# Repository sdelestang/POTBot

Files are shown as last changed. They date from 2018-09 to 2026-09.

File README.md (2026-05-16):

# POTBot

**Smart camera systems for tracking climate change underwater in fish and habitats.**

POTBot is an open-source, Arduino-based automated underwater camera and environmental monitoring system. Originally developed for deployment inside commercial western rock lobster pots, the system records video of marine habitats and faunal communities at fishing locations, logs water temperature, and captures GPS coordinates on retrieval.

The system operates autonomously for approximately one month of continuous fishing activity. When spent, units are simply swapped out for fresh ones and data collection continues at minimal cost.

## How It Works

1. **Power on** — the unit acquires a GPS lock and enters standby.
2. **Deployment** — a conductivity-based wet switch detects immersion and triggers video recording.
3. **In water** — the camera records for a configurable duration (default 40 min). Water temperature is logged periodically. If deployed in darkness, a short supplementary video is recorded at dawn.
4. **Retrieval** — when removed from water, the GPS activates and records the pot's position.
5. **Data download** — videos are accessed via USB from the Mobius camera; metadata (GPS, timestamps, temperatures) is read through the Arduino Serial Monitor.

## Repository Structure

```
POTBot/
├── docs/
│   ├── POTBot_Operations_Manual.docx   # Full setup and operations manual
│   └── Flow_Diagram_PB_IV.jpg          # Operational state diagram
├── Version10/
│   └── PB_CodeV10/
│       └── PB_CodeV10.ino              # Current firmware (V10)
├── Pot_code/                           # Earlier firmware versions
├── Final-Report 2011-021.pdf           # Original FRDC research report
└── README.md
```

## Hardware

| Component | Description |
|-----------|-------------|
| Microcontroller | Adafruit ItsyBitsy M0 Express |
| Camera | Mobius ActionCam |
| GPS | Serial GPS module (9600 baud) |
| Real-Time Clock | Gravity RTC (I²C) |
| Temperature Sensor | Dallas DS18B20 (OneWire) |
| Flash Storage | Adafruit SPI Flash (onboard FAT filesystem) |
| Status LED | Adafruit DotStar |
| Wet Switch | Conductivity-based (analog) |

## Getting Started
### Download all files inclusing the manual
Download the firmware from GitHub. Navigate to https://github.com/sdelestang/POTBot and click the green “Code” button, then select “Download ZIP”. Save and extract the ZIP file to a convenient location on your computer (e.g. C:\POTBot).

### Prerequisites

- [Arduino IDE](https://www.arduino.cc/en/software) (latest version)
- Adafruit SAMD board support (install via Boards Manager)
- Required libraries (install via Library Manager):
  - OneWire
  - DallasTemperature
  - Adafruit SleepyDog
  - Adafruit SPIFlash
  - TinyGPS++
  - Adafruit DotStar
  - RTClib
- GravityRTC library (install from ZIP — included in the repo or available in the docs)

### Upload Firmware

1. Open `Version10/PB_CodeV10/PB_CodeV10.ino` in Arduino IDE.
2. Select **Adafruit ItsyBitsy M0** as the board.
3. Select the correct COM port.
4. Click Upload.

For detailed setup, deployment, and data retrieval instructions, see the **[Operations Manual](docs/POTBot_Operations_Manual.docx)**.

## Configurable Parameters

| Parameter | Default | Unit | Description |
|-----------|---------|------|-------------|
| `VidTime` | 2400 | seconds | Video recording duration after deployment |
| `GPSTime` | 240 | minutes | GPS active time after retrieval |
| `Dawn` | 7 | hour (24h) | Start of daylight window |
| `Dusk` | 17 | hour (24h) | End of daylight window |

## Applications

POTBot systems have been used to:

- Augment spatial habitat mapping off the west coast of Western Australia
- Document spatial and habitat distributions of marine teleosts across the west coast bioregion
- Serve as a robust, automated alternative for BRUV (Baited Remote Underwater Video) monitoring with geographic synchronisation of footage

## Licence

This project is open-source freeware. See individual files for any specific terms.

## Contributing

Contributions, bug reports, and feature requests are welcome. Please open an issue or submit a pull request.

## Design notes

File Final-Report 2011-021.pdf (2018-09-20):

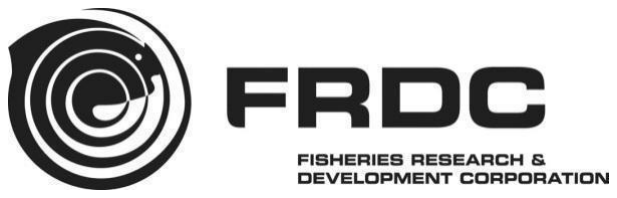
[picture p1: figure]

1

# Development of an industry-based habitat mapping/monitoring system

Matthew Pember, Simon de Lestang and Dirk Slawinski

2017

FRDC Project No 2011/021

2

© Year Fisheries Research and Development Corporation. All rights reserved.

ISBN [Insert ISBN/ISSN – researcher to obtain - TBA]

Development of an industry-based habitat mapping/monitoring system 2011/021

2017

Ownership of Intellectual property rights
Unless otherwise noted, copyright (and any other intellectual property rights, if any) in this publication is owned by the Fisheries Research and Development Corporation.

This publication (and any information sourced from it) should be attributed to Pember, M., de Lestang, S. & Slawinski,
D. Department of Primary Industries and Regional Development; Fisheries Division, Western Australia, 2017, Development of an industry-based habitat mapping/monitoring system, Perth, Western Australia, July.

Creative Commons licence
All material in this publication is licensed under a Creative Commons Attribution 3.0 Australia Licence, save for content supplied by third parties, logos and the Commonwealth Coat of Arms.

Creative Commons Attribution 3.0 Australia Licence is a standard form licence agreement that allows you to copy, distribute, transmit and adapt this publication provided you attribute the work. A summary of the licence terms is available from creativecommons.org/licenses/by/3.0/au/deed.en. The full licence terms are available from creativecommons.org/licenses/by/3.0/au/legalcode.

Inquiries regarding the licence and any use of this document should be sent to: frdc@frdc.com.au

Disclaimer
The authors do not warrant that the information in this document is free from errors or omissions. The authors do not accept any form of liability, be it contractual, tortious, or otherwise, for the contents of this document or for any consequences arising from its use or any reliance placed upon it. The information, opinions and advice contained in this document may not relate, or be relevant, to a readers particular circumstances. Opinions expressed by the authors are the individual opinions expressed by those persons and are not necessarily those of the publisher, research provider or the FRDC.

The Fisheries Research and Development Corporation plans, invests in and manages fisheries research and development throughout Australia. It is a statutory authority within the portfolio of the federal Minister for Agriculture, Fisheries and Forestry, jointly funded by the Australian Government and the fishing industry.

Researcher Contact Details | FRDC Contact Details
Name: Matthew Pember Senior Resource Access Officer Address: 56 Marine Tce, Fremantle 6160 WA Phone: +61 08 9432 7777 Fax: +61 08 9432 7700 Email: rao@wafic.org.au | Address: Phone: Fax: Email: Web: 25 Geils Court, Deakin 2600 ACT 02 6285 0400 02 6285 0499 frdc@frdc.com.au www.frdc.com.au ,

In submitting this report, the researcher has agreed to FRDC publishing this material in its edited form.

3

## Contents

Acknowledgments | 6
Abbreviations | 6
Executive Summary | 7
Introduction | 11
Objectives | 12
Methods/Results | 13

Objective 1. Development of a cost-effective system for obtaining geo-referenced environmental
information. | 13
POTBot functionality | 14
POTBot development | 14
Initial design | 14
Component Choice | 16
Controller | 16
Camera | 16
GPS | 20
Temperature Sensor | 21
Data Storage | 21
Power Source | 21
Additional Supporting Components | 22
Water Proof Housing | 22
Placement in a lobster pot | 24
Physical layout and construction | 24
Programming | 26
Objective 2. Trial implementation of system by industry to test concept. | 27
Performance of POTBot v2 and 3 | 29
Objective 3. Cost-benefit analysis with conventional ground-truthing techniques. | 30
Comparison of habitat mapping at the Leeman Closed area | 30
Comparison of visual-based fin-fish monitoring | 33
Discussion | 35

Objective 1: Development of a cost-effective system for obtaining geo-referenced environmental

4

information. | 35
Objective 2: Trial implementation of system by industry to test concept. | 36
Objective 3: Cost-benefit analysis with conventional ground-truthing techniques. | 37
Conclusion | 38
References | 39
Implications | 41
Recommendations | 41
Further development | 41
Extension and Adoption | 41
Project Coverage | 42
Project Materials Developed | 43
Appendix 1. | 44
Appendix 2. POTBot code. | 45

## Tables

Table 1. List of the potential functionality of the POTBot and their associated importance, cost and difficulty of implementation. Grey rows represent functions chosen for implementation into the initial
model. | 20
Table 2. Spy camera trialled and their respective picture qualities. The camera chosen for integration
into POTBot v1 Is highlighted in grey. | 23
Table 3. Upgraded cameras for use in POTBot versions 2-4. | 25
Table 4. Component costs for the development of POTBot version 3. | 30

## Figures

Figure 1. Evolution of the various versions of the POTBot. | 19
Figure 2. Wiring schematic of the POTBot, with permanent connections shown as solid lines and intermittent connections as dotted lines. Red, black and blue lines denote positive, negative and serial (data) connections, respectively. Transistors (T) and resistors (R) are shown. The external wires shown at the middle right are the wires running to the external of the water housing to detect the presence of water.
| 24
Figure 3. Schematic of the PCB board for the POTBot. | 29
Figure 4. Flow diagram showing business rules followed by the POTBot versions 1-3 and its subsequent

5

behaviour. | 32
Figure 5. Map illustrating the spatial distribution of more than 1300 pot camera deployments made during research and normal commercial lobster fishing activities. The inset shows the key habitat categories observed inside and surrounding the research area at Leeman that is closed to lobster fishing and where
high resolution bathymetric information was collected as part of FRDC 2008/013. | 34
Figure 6. Relative causes resulting in a habitat classification not occurring from a POTBot deployment. | 35

## Plates

Plate 1. Breadboard linking power to an integrated circuit and an 808 camera, using a signal relay to connect a junction across the shutter button on the camera (paired white wires) (photo from
http://quinndunki.com/blondihacks/?p=925). | 17
Plate 2. High-pressure PVC pipe fitting housings used in POTBot v 2 and 3, showing clockwise from top right; entire housing with black screw cap on left, water sensing screw pins towards the centre and lens located on the right; closer shot of the water sensing screw pins with associate glue to ensure a tight seal; internal view of the housing showing the wires connected to the internal aspect of the screw pins; front of
the housing with its clear Perspex lens. | 23
Plate 3. Schematic of a lobster pot showing the location of the POTBot. | 29
Plate 4. POTBot built on purpose-made PCB (green) with camera at the front, GPS visible towards the back and battery and Arduino mini located under the PCB; PVC underwater housing capable of deployments to
greater than 180 m. | 30

6

## Acknowledgments

We would like to thank Fisheries Research and Development Corporation for their financial support and all

of the commercial rock lobster fishers who agreed to run POTBot systems in their fishing gear. We would

also like to thank Ainslie Denham for help with the geo-statistical work in this report and Lachlan Strain,

Scott Evans, Nick Blay and Nick Caputi for their help in reviewing.

## Abbreviations

BRUVs: Baited Remote Underwater Video Systems

CSIRO: The Commonwealth Scientific and Industrial Research Organisation.

DPIRD FD: Department of Primary Industries and Regional Development, Fisheries Division. Western Australia

FRDC: Fisheries Research and Development Corporation

MSC: Marine Stewardship Council

NMEA: National Marine Electronics Association

PCB: Printed Circuit Board

PCM: Pulse Code Modulation

POTBot: Pictures Of The Bottom

UWA: University of Western Australia

WCRLMF: West Coast Rock Lobster Managed Fishery

WAMSI: West Australian Marine Science Institution

7

## Executive Summary

Mapping / monitoring in the marine environment can be a very costly exercise. Scientists from the

Department of Primary Industries and Regional Development; Fisheries Division (FD) and the

Commonwealth Scientific and Industrial Research Organisation (CSIRO) have developed a small, low-cost

automated camera system that, when fitted to commercial fishing gear, can achieve this at minimal cost.

The POTBot (Pictures Of The Bottom) system is a cheap, small “smart” camera that can track its position

globally and the date and time, and can record high-definition video and water temperature readings when it

determines it has been deployed into the ocean.

Initially developed to be attached to pots in the West Coast Rock Lobster Managed Fishery (WCRLMF), the

POTBot system collects vision of the habitats and the faunal communities where fishing gear has been set,

and lasts for about a month of continuous commercial lobster fishing activity. When out of power, systems

are simply swapped out for fresh ones / recharged and the collection of data continues at minimal costs.

Trials of the POTBot system conducted during this study have proved extremely valuable and have been

used to augment the development of a number of spatial habitat maps off the west coast of Western

Australia, as well as document the spatial and habitat distributions of a number of marine teleosts

throughout the west coast bioregion. The POTBot systems have also proved to be a very valuable system

for use in Baited Remote Underwater Video Systems (BRUVs) monitoring due to their robustness,

automated capabilities and the geographic synchronisation of their footage.

The success of this project is highlighted by current plans to incorporate POTBot systems on a long-term

basis into standard research programs: Western Rock Lobster monitoring program, FD BRUV monitoring

programs and two recently approved Fishery Research and Development Corporation (FRDC) projects

being conducted by the University of Western Australia (UWA). A number of interstate and overseas

research institutes have also shown interest in obtaining this technology for use in their own research

environments.

Background

A thorough appreciation of the nature and extent of the habitats a fishery operates across, and possibly

impacts upon, is fundamental to the effective implementation of ecosystem-based fisheries management.

The significance of reliable habitat information to sustainable management is highlighted by the fact that it

may be considered a prerequisite for fisheries seeking to obtain, or retain, ecologically sustainable

certification such as Marine Stewardship Certification (MSC).

In the case of the Western Rock Lobster Panulirus cygnus, current and recently completed projects (FRDC

2004/049, 2008/013) and the West Australian Marine Science Institution (WAMSI) node 4.3 (Corals of the

northwest of Western Australia) have illustrated that the composition of benthic habitats may have a strong

influence on the demographics of exploited species. While these projects provided high resolution

8

information on benthic habitats at key locations, areas currently mapped at high resolution represent < 1% of

the WCRLMF. The ability to expand mapping at a similar resolution was constrained by the large costs

involved with current mapping techniques, e.g. multibeam sonar. In a recent audit report the MSC certifying

body accepted the futility of expanding these surveys with high cost techniques and suggested a more

broad-scale approach should be adopted in mapping the distribution of habitats in the WCRLMF.

Aims / Objectives

This project aimed to develop and trial the implementation of a cost effective tool for the ongoing collection

of geo-referenced environmental information, including data on the composition and distribution of benthic

habitats. The concept arose from the realisation that opportunities exist for greater industry involvement in

collection of oceanographic and habitat data. Commercial Wester Rock Lobster fishers set pots on a daily

basis and low-cost technologies are now available that have the potential to give them the ability to collect

high resolution habitat data. Information could be collected across a broad spatial scale with no added cost

or interruption to their fishing operation. The key objectives of the study were:

1. Development of a cost-effective system for obtaining geo-referenced environmental information.
2. Trial implementation of system by industry to test concept.
3. Cost-benefit analysis with conventional ground-truthing techniques.

Methodology

The project focussed on each objective sequentially. As such initial work was conducted on developing a

POTBot system prototype. The requirements for the system were determined through interviews with

marine scientists. The POTBot was designed to undertake a range of programmed tasks based on its

detection of the presence of seawater (e.g. if the system was submerged or not).

Testing of prototypes was conducted in two phases: Initial laboratory testing and extended in situ testing.

a) Initial testing / selection of components was conducted within the laboratory (aquaria) at FD. This included

activities such as submersion tests, image quality, power consumption and accuracy of measurements (e.g.

global position and water temperature).

b) Extended testing was conducted in the field on board FD research vessels. This examined the

components under working conditions and allowed for the refinement of programming to the behaviour of

typical fishing operations.

Trial implementation of the system by industry followed on after FD field trials. A number of interested

commercial Wester Rock Lobster fishers spanning the WCRLMF were provided with POTBot systems (~20

fishers) between 2012 and 2015. These trials tested the robustness of the POTBots to a commercial fishing

operation, commercial fisher’s acceptance of units in their pots and collected initial habitat information

9

throughout the WCRLMF.

A cost-benefit analysis comparing the POTBot system with conventional ground-truthing techniques was

then conducted to help assess the value of implementing an on-going monitoring program using the system.

As part of FRDC project 2008/013, a deep-water location in the WCRLMF was ground-truthed using the

traditional techniques of drop-camera and towed video. These data and their associated costs have been

fully recorded by the FD. As additional monitoring of the lobster population in this area occurs annually, it

proved an ideal opportunity to fit POTBot systems into these pots and re-map the area using this innovative

technology at no extra cost. The two sets of ground-truthed data were compared via geostatistical

techniques, with indicator variables of the presence or absence of each habitat type being compared. The

cost associated with the collection of the two sets of data was also compared.

A second cost-benefit analysis was undertaken following the use of POTBot videos to conduct an

assessment of the spatial and temporal distributions of a number of key teleosts along the western

Australian coast, from Kalbarri in the north to Mandurah in the south (Brooker et al. submitted). This study

was compared to a study with a similar spatial coverage based on BRUV systems (Langlois et al., 2012).

Again the ability of the two studies to determine teleost distributions and their associated costs have been

compared.

Results / Key findings

This project was successful in developing a low cost automated geo-referencing camera system that can be

deployed throughout a number of commercial fishing operations (i.e. operations which deploy fishing gear).

At a unit cost of approximately $250 this technology is far more accessible for wide-scale implementation

than other, less autonomous products available (e.g. GoPro at ~$500 unit⁻¹
).

The success of developing the POTBot was partly attributable to the recent rapid increase in the

development of micro-electronic systems and robotics. Over the course of the project both lithium-polymer

batteries and high-definition “spy” cameras became widely available in a range of sizes and at markedly

reduced prices. Micro-controllers have also increased in their diversity and reduced in cost. This has

allowed the POTBot to maintain a small size as well as low cost.

Analysis of both research and industry collected data is continuing. The collated habitat information has

provided a map of the key habitats fishers operate across the extent of the WCRLMF and is currently being

used to validate the fishery-wide habitat maps that have been developed from the outputs of a previous

FRDC project (2008/013). These projects have directly resulted in the MSC re-certification of the Western

Rock Lobster Fishery becoming free, for the first time, of any conditions under Principle 2 (Minimising

environmental impact: What are the impacts? Fishing activity must be managed carefully so that other

species and habitats within the ecosystem remain healthy). These projects have shown that there are no

discernible impacts on the wider ecosystem from the Western Rock Lobster fishery.

10

Examination of fish community data from POTBot deployments highlighted the units’ versatility and cost-

effectiveness as a fisheries monitoring tool that can be deployed using existing infrastructure. Although

comparison against spatio-temporal variation in similar fisheries-independent or -dependent indices is

required, preliminary results suggest that the method has potential as an alternative means for monitoring

relative abundance of fin-fish.

POTBots were capable of producing data used to develop a habitat map that showed good agreement to a

fine-scale high resolution map produced by combining a number of different methods including expensive

side-scan sonar. This comparison shows that the use of POTBots can produce habitat maps far cheaper

than can be produced based on the more traditional techniques of towed video and drop camera, especially

if an area is to be fished for a separate purpose (e.g. fishery survey). Furthermore, the comparison with a

BRUV fin-fish project suggests that the monitoring of marine fauna can also be conducted using POTBots at

a fraction of the cost, so long as the area of the study is shared with a commercial fishery willing to adopt the

POTBot fishing program.

Recommendations

The POTBot system developed during this study proved to be an extremely useful research tool. This has

been highlighted by the fact that data collected during this project has already been used to describe the

faunal composition of teleosts along the mid-west coast of Australia, as well as to augment the development

of habitat maps throughout the same area. Through the use of this technology, information on habitats in

remote areas has been recorded for the first time, information that will be valuable when determining long-

term environmental changes in the future. Such a case has already occurred following the marine heatwave

of 2010/11. It is recommended that, when appropriate, this technology be adopted by other research

institutions to gather this previously inhibitively expensive data and long term data sets should start to be

collated.

Keywords

Camera, POTBot, BRUV, marine, habitat, mapping, lobster fishery

11

## Introduction

A thorough appreciation of the nature and extent of the habitats a fishery operates across, and possibly

impacts upon, is fundamental to the effective implementation of ecosystem based fisheries management.

Understanding the relationships between benthic habitats and the species they support not only allows

fishery managers to control against any potentially undesirable impacts on habitats, but also permits

management to be more adaptive and spatially explicit. The significance of reliable habitat information to

sustainable management is highlighted by the fact that it may be considered a prerequisite for fisheries

seeking to obtain, or retain, ecologically sustainable certification, i.e. MSC certification.

In the case of the Western Rock Lobster Panulirus cygnus, current and recently completed projects

(FRDC 2008/013, 2004/049 and WAMSI 4.3) have illustrated that the composition of benthic habitats may

have a strong influence on the demographics of exploited species. While these projects provided high

resolution information on benthic habitats at key locations, areas currently mapped at high resolution

represent < 1% of the WCRLMF. The ability to expand mapping at a similar resolution is constrained by the

large costs involved with current mapping techniques, e.g. multibeam sonar. In a recent audit report the MSC

certifying body accepted the futility of expanding these surveys with high cost techniques and suggested a

more broad-scale approach should be adopted in mapping the distribution of habitats in the WCRLMF.

This project aims to develop and trial the implementation of a cost effective tool for the ongoing collection of

geo-referenced environmental information, including data on the composition and distribution of benthic

habitats. The concept arose from the realisation that opportunities exist for greater industry involvement in

collection of oceanographic and habitat data. Commercial Western Rock Lobster fishers are setting pots in

benthic habitats on a daily basis and low-cost technologies are now available that have the potential to give

them the ability to collect high resolution habitat data. Information could be collected across a broad spatial

scale with no added cost or interruption to their fishing operation.

The cost effectiveness of this system is the product of an innovative use of relatively inexpensive technology

and the direct involvement of stakeholders in data collection. Recently, fishers have participated in a study

using modified research pots where the location of pot sets is recorded along with catch information. In

addition to detailed demographic data, that project is beginning to provide researchers with a broad-scale

picture of the spatial distribution of fishing operations across different parts of the WCRLMF and fishing

season. Outputs of the modified pot trials could be greatly expanded if habitat information could be easily

collected for each pot set.

Besides informing researchers and managers of the broad-scale habitat patterns found across the

WCRLMF, this system could represent a cost-effective method of collecting the habitat information required

to validate predictive habitat models. Furthermore, the information provided will fine-tune habitat / Western

Rock Lobster relationships developed in previous projects. Wide and continuous deployment of systems

throughout the WCRLMF will allow researchers to quantify how such relationships change with latitude and

12

depth and vary temporally.

In addition to mapping habitat, these technologies are capable of collecting a range of other important data

including spatial information on salinity, water temperature and depth, and the relative abundance / species

composition of finfish. Ultimately, increased knowledge of the interactions between the environment and

exploited species will foster more holistic and adaptive fisheries management. While the project concentrates

on the fishery for the Western Rock Lobster in a proof of concept study, the technologies have far wider

applications, particularly for small or data poor fisheries.

A thorough understanding of the relationships between benthic habitats, exploited species and the fisheries

they support increases the capacity for fisheries management to be ecologically sustainable and adaptive in

the face of climate change and spatial zoning.

Improving knowledge of such relationships typically requires a significant commitment of resources, i.e.

swath-mapping and dedicated ground truthing. Costs are prohibitive of continuous spatial coverage and the

snap-shot nature of data acquisition provides little confidence that habitat relationships persist through time.

There is a real need for a more cost-effective approach to collecting oceanographic and habitat information.

This project develops and implements a system capable of providing constantly updating, geo-referenced

environmental data, including information on the composition of benthic habitats.

This project addresses key priorities of FRDC’s Ecological Sustainable Development theme. Specifically, the

project will:

- develop a cost-effective tool that aids in the implementation of ecosystem-based fisheries management.
- improve the acquisition and incorporation of environmental / habitat data into fisheries management.
- improve knowledge of key biological attributes for target species.

In addition, this project contributes to other environment related RD&E priorities by:

- informing on the likelihood, and thus mitigating the impacts, of fishing activities on aquatic habitats and

ecosystems.

- providing a tool to monitor fishing gear interactions with non-target species.
- contributing to industry’s ability to adapt to climate change by providing a tool to monitor real-time changes

to oceanographic conditions, benthic habitats and relationships with exploited species.

In the case of the Western Rock Lobster, this research ensures continued MSC certification by addressing

requirements that “the nature and distribution of habitats relevant to the fishing operations is known”.

However, the needs addressed by the project are not specific to the WCRLMF. This technology is

transferable to other fisheries and has particular application to data poor fisheries.

## Objectives

1. Development of a cost-effective system for obtaining geo-referenced environmental information.
2. Trial implementation of system by industry to test concept.
3. Cost-benefit analysis with conventional ground-truthing techniques.

13

## Methods/Results

## Objective 1. Development of a cost-effective system for obtaining geo-referenced

environmental information.

The cost-effective system for obtaining geo-referenced environmental information has been named POTBot.

The model that was used for field trials and the cost-benefit analysis was the third product in a series of

prototypes that were developed. The evolution of the various prototypes was due to the concurrent

expansion and increase in accessibility of micro-computers, batteries and camera systems. What was

available and possible at low cost towards the end of the project was substantially different from what was

available at the beginning. The evolution in development of the POTBot is shown in Figure 1 and described

below.

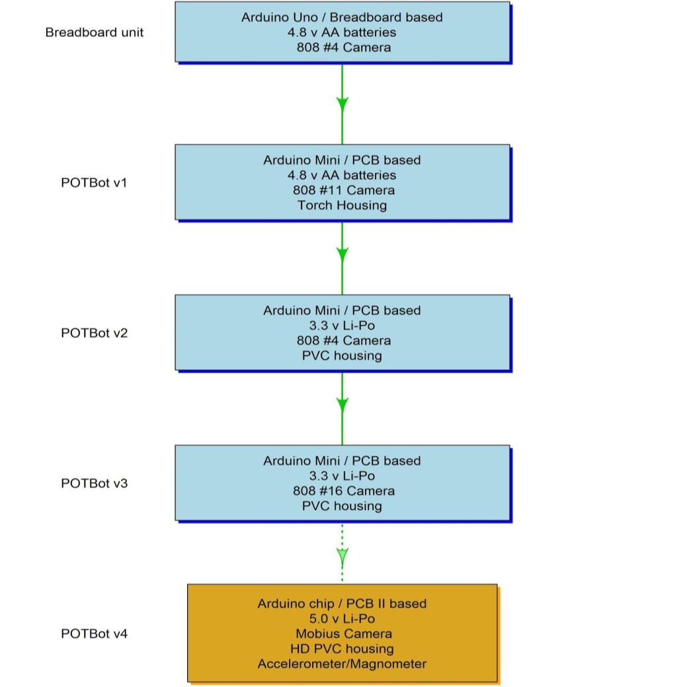
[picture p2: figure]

Figure 1. Evolution of the various versions of the POTBot. Note version 4 was developed subsequent to the analyses described in this report.

14

POTBot functionality
In order to develop the camera system, literature and internet reviews were first conducted to determine what

functions were available that could be incorporated into the system. This included contacting other marine

researchers to see what was on their “wish list” for such a device. The potential functionality of a POTBot

system was then compiled from the reviews along with their associated general costs and ease of

implementation (Table 1).

Table 1. List of the potential functionality of the POTBot and their associated importance, cost and difficulty of implementation. Grey rows represent functions chosen for implementation into the initial model.

Functionality | Importance | Implementation Difficulty | Relative cost
Good quality vision (1280 x 720 pixels) | 3 | 1 | 2
High Definition vision (1920 x 1080 pixels) | 2 | 2 | 2
Stereo vision (twin lenses) | 1 | 2 | 2
Determine position (GPS) | 3 | 1 | 2
Lights | 1 | 3 | 2
Data storage | 3 | 1 | 1
Measure temperature | 2 | 1 | 1
Measure salinity | 1 | 3 | 2
Measure depth | 2 | 3 | 3
Measure orientation / movement | 1 | 1 | 1
Measure water movement / current | 1 | 3 | 3
Depth rated to 100 m | 3 | 1 | 1
Depth rated to 200 m | 2 | 2 | 2
Depth rated to 1000 m | 1 | 3 | 3
Small size | 3 | 2 | 2
Long battery life (>30 days) | 3 | 3 | 2
Ease of use | 3 | 2 | 2
Blue-tooth connectivity | 1 | 3 | 3
Wireless charging | 1 | 3 | 2

1 = low, 2 = medium, 3 = high

From the review process it was considered possible that a basic model could be developed that contained all

of the high priority functions fairly easily (grey rows in Table 1). As such it was decided to initially develop

this basic version for trials prior to examining the possibility of upgrading various aspects. The initial model

included the capabilities of the functions highlighted by the grey rows in Table 1 (POTBot v1).

POTBot development

Initial design
Once the general capabilities of the system had been determined a second review process was undertaken

15

to determine whether:

- a system such as POTBot v1 currently existed;
- a similar system existed that could be modified to suit our purposes;
- the components of POTBot v1 existed and could be amalgamated to suit our purposes;
- the components did not all exist and some would have to be built from the ground-up.

A number of camera systems were available for sale, of which some were water proof (with associated

housings), some were programmable and could geo-reference images/video, some were small and some

had low power demands. However, no pre-made systems were found that provided the entire functionality of

POTBot v1.

A number of systems that had similar functionality to POTBot v1 already existed and essentially only needed

waterproof housings developed. These systems were smart phones. They contain cameras with geo-

referencing capabilities, magnetometers and accelerometers to determine orientation and acceleration,

respectively, and data storage capabilities. They also could utilise external power sources to extend their

run-time into weeks. There were however, two main limitations to adapting a smart phone into POTBot v1.

They are relatively expensive (> $400 per unit) and they required custom-made waterproof housings. A

housing to fit a rectangular object with a camera on its largest face (standard smart phone layout) requires

either a rectangular housing or a relatively large cylindrical housing. An objective of the project was to

develop a small unit so the large cylindrical housings were not considered appropriate. Rectangular

housings presented structural issues for deployment at depth and were therefore very difficult and expensive

to construct (> $300 per unit). The programming of mobile phones further requires specialised skills as their

software platforms have very technical solutions to problems such as power saving, which are quite difficult

to modify to suit the requirements of the POTBot v1. As such it was not considered the best course of action

to re-purpose a smart phone.

The various components of the POTBot v1 system were found to already exist, with the majority of functions

capable of being completed by a number of different components, thus providing choice. This diverse range

of products available allowed their accessibility and cost to be factored into whether they were chosen to be

integrated. For example, for the video camera alone over 50 products fitted the brief of being small,

providing a minimum of 1280 x 720 pixel resolution, having relatively low power demands, being externally

controllable and having a relatively low cost. Another advantage of integrating specific components was the

removal of superfluous components with their associated power demands. For example, a smart phone will

poll for and analyses phone signal coverage strength. This unnecessarily utilises power and is not required

for integration in the POTBot v1. Therefore the option of combining specific components proved to be the

most power conservative. The development of POTBot v1 from pre-existing components was chosen as the

best model.

16

Component Choice

Controller
To achieve the chosen functionality of POTBot v1 the system needed a camera, GPS, temperature sensor

(thermistor), data storage unit, power source and water proof housing. The system also needed a central-

controlling unit, something to turn the camera on and off, determine the geographic position and record this

information. Of the available options it was initially clear that one of the many micro-controllers available was

a good option ($15 - $50), with the open-source nature of their software and large communities providing

online scripting help. Controllers compared were the BeagleBone units (https://beagleboard.org/), Raspberry

Pi units (https://www.raspberrypi.org/) and Arduino units (https://www.arduino.cc/). Generally the three

platforms had similar functionalities and capabilities, with the main difference being the Arduino’s lower

power usage (due in part to its lower processor power). The Arduino also had the ability to enter into a sleep

mode, thus further reducing (66%) its power usage. The very small footprint of the Arduino Mini, its low cost

(~$15) and its ability to run on either 3.3 or 5 v made this board our choice for controlling the POTBot v1

(https://www.arduino.cc/en/Main/arduinoBoardMini). However, due to the mini’s small size and design, an

Arduino Uno (https://www.arduino.cc/en/Main/ArduinoBoardUno) was initially used for the development and

solderless bread boarding of POTBot v1 (Plate 1; a board containing a number (+50) of interconnected pins

that allow easy connection of a number of wires/components: see https://en.wikipedia.org/wiki/Breadboard

for more information on breadboards). The main features of the Uno that made it more appropriate for the

development stage was its pin structure, which did not require soldering (header pins are pre-built) and the

easier serial connection of the Uno to the computer for two-way communication (i.e. uploading software and

receiving Arduino outputs).

Camera
A number of small camera units were examined and trialled. The recent boom in the prevalence of small

low-cost spy-cameras proved beneficial for this project. The benefits of these camera units was that they

were all very cheap ($1 - $40) and small (< 50 mm long and <10 mm thick), they contained very advanced

post processing software for compressing large video files and storing all of the footage on small microSD

cards, they all use 3.3 v power sources (can generally handle from 3 – 5 v) and their usage is simplified

(minimal button presses to take and stop video footage). The only real limitation of these cameras was the

quality of some of the unit’s footage (even though they were described as 1280 x 720 px). As such twelve

commonly advertised “spy” cameras were purchased and trialled. A list of these initial cameras trialled, their

cost and sources are listed in Table 2.

Of the twelve spy cameras trialled the Mini 808 Car Key Chain Micro Camera HD 720P #4 was chosen for

integration into POTBot v1 due to its good quality video and low price ($25). This camera contained two

push-button switches to turn it on and off and to start and stop videos being recorded. This camera could be

controlled by the micro-controller board through the soldering of two wires onto opposite poles of each of the

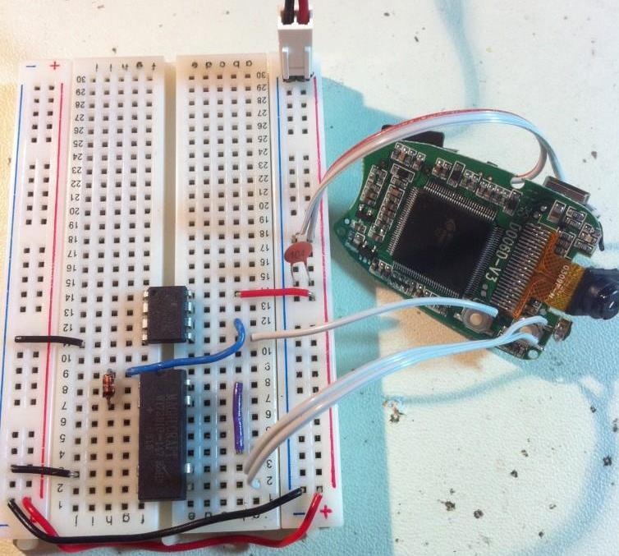
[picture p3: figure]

17

two switches and allowing the controller to ”join” these wires thus replicating a press of the switch (Plate 1).

The joining of the two wires was achieved using a NP transistor (Figure 2 & Figure 3). Although not true

1280 x 720 px (the frame is up scaled from 640 x 480 px with interpolation making it appear to be 1280 x 720

px) the quality of the video was more than sufficient, especially for the development phase. The power usage

of this camera was 130 mA when on but not recording and 160 mA when recording a video.

Plate 1. Breadboard linking power to an integrated circuit and an 808 camera, using a signal relay to connect a junction across the shutter button on the camera (paired white wires) (photo from http://quinndunki.com/blondihacks/?p=925).

18

Table 2. Spy cameras trialled and their respective picture qualities. The camera chosen for integration into POTBot v1 is highlighted in grey.

Camera name | Source | Cost | Picture quality
Mini DV Spy Lighter Camera Hidden Camera Video Recorder | Ebay #190447659725 | $1.84 | Low
New 808 Keychain Key chain keyring mini spy camera DVR #1 | Ebay #370430370782 | $2.50 | Low
808 #3 Car Key Spy Camera fob Camcorder keyring | Ebay #150567816880 | $24.00 | Medium
Mini 808 Car Key Chain Micro Camera HD 720P #4 | Ebay #110280524362 | $24.95 | High
Mini DV Spy Lighter Camera Hidden Camera Video Recorder | Ebay #190447659725 | $19.56 | Medium
909 Mini Car Keys Shape DVR Spy Camera support TF card | Ebay #320612800707 | $16.99 | Medium
Flashlight Video Camera Spy MINI DV LED Night vision-IR | Ebay #400170448477 | $29.99 | High
Mini DV DVR Sports Video Camera Spy cam MD80 spycam DC | Ebay #170477360104 | $12.65 | Medium
NEW HD 1280*960 Hidden Spy Mini DV Camera Video Cam Camcorder Motion Detection | Ebay #320779431551 | $39.20 | High
NEW 8GB HD 1280 x 960 Hidden Spy Mini DV Camera Video Camcorder Motion Detection | Ebay #170791427941 | $39.95 | High
Mini GSM SIM Card Hidden Spy Camera Audio Video Record X009 DV Ear Bug Monitor | Ebay #400963922767 | $19.28 | Medium

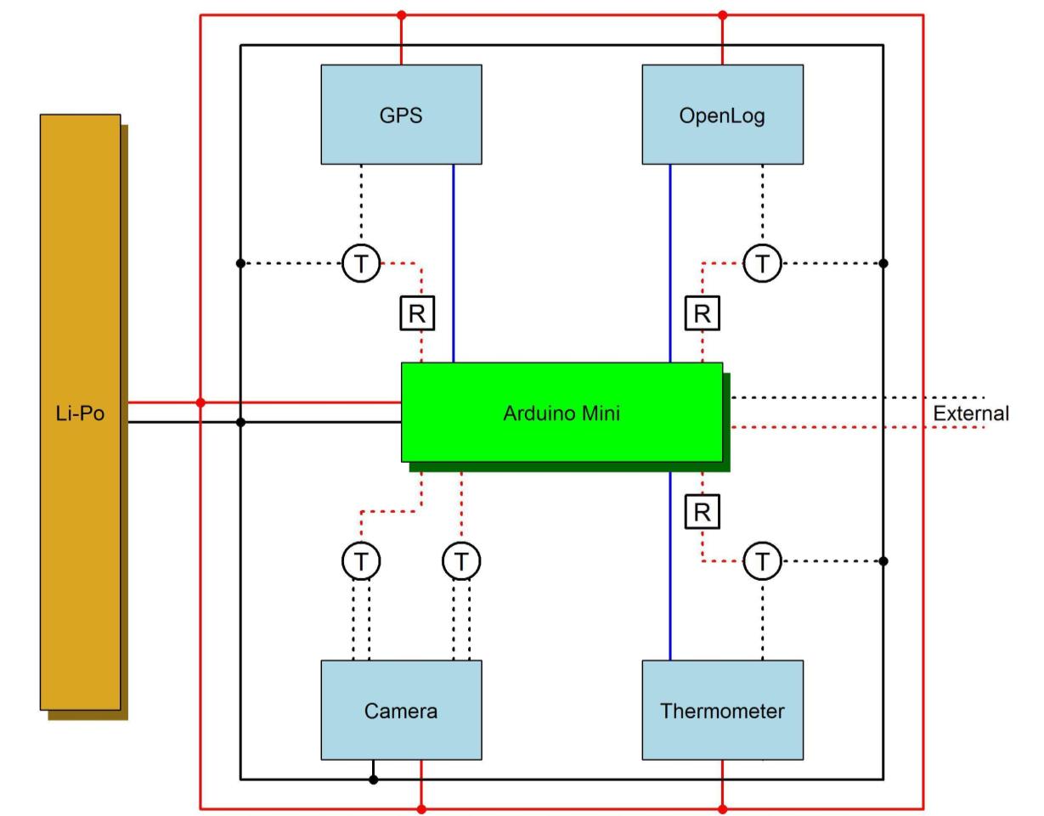
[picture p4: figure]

19

Figure 2. Wiring schematic of the POTBot, with permanent connections shown as solid lines and intermittent connections as dotted lines. Red, black and blue lines denote positive, negative and serial (data) connections, respectively. Transistors (T) and resistors (R) are shown. The external wires shown at the middle right are the wires running to the external of the water housing to detect the presence of water.

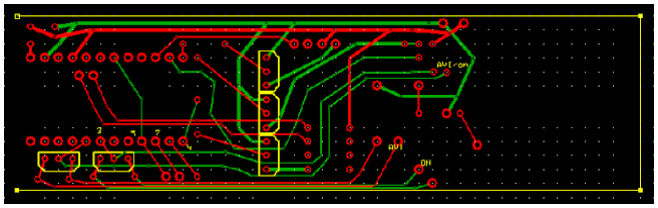
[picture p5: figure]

Figure 3. Schematic of the PCB board for the POTBot.

Following on from the initial development of POTBot v1 a number of improved versions of the 808 camera

model were released (#11 in early 2012, #16 in mid-2012 and Mobius in early 2013). These versions had

20

increased picture quality (full high definition: 1920 x 1080 px) as well as a 120o wide-angle lens and greater

functionality. The #16 and Mobius could be pre-programmed (e.g. adjust auto-shut off and power down and

video frame rates); with the Mobius capable of being programmed to take a video simply on power-up (did

not therefore need its buttons to be triggered by the micro-controller). Although more expensive than the

original #4 camera used in POTBot v1 the increases in price were outweighed by the increased performance

of these cameras. As such the #11, #16 and Mobius were each included into sequential POTBot versions 2-

4, respectively (Table 3).

Table 3. Upgraded cameras for use in POTBot versions 2-4.

Camera name | Source | Cost | Picture quality
HD #11 Spy Camera Car Keychain DVR Video MOV Record 808 | Ebay #110710564362 | $38.98 | High
808 #16 Car Key Chain Micro Camera Real HD 720P H.264 Pocket Camcorder Lens C | Ebay #291416261090 | $45.21 | High
Mobius Action Camera Full HD 1080P 30FPS 720P 60FPS Sports Cam FPV Camcorder | Ebay #351678603738 | $64.34 | High

Global Positioning System
The Global Positioning System chosen was a PMB-648 GPS SiRF integrated with an internal antenna. The

PMB-648 GPS module provides high performance with a SiRFstarIII chipset and integrated patch antenna.

This was one of the more expensive internal components at $34.99 (Sales@Parallax.com). The PMB-648

GPS features 20 parallel satellite-tracking channels for fast acquisition of NMEA0183 v2.2 data. It has a

patch antenna; rechargeable battery for memory and Real Time Clock (RTC) backup; cable for power, and

Transistor–Transistor Logic (TTL) and Recommended Standard-232 (RS-232) connections. This GPS

proved very easy to use and incorporate into the POTBot v1. In its most basic setup the unit only requires to

be powered and it automatically searches for satellites and returns NMEA data (National Marine Electronics

Association). The NMEA standard is formatted in lines of data called sentences, with each sentence

containing various bits of data organized in comma delimited format. The sentence chosen to strip out the position (latitude and longitude) and date/time was denoted by the header code “$GPRMC”, which contained

a range of information including a time stamp, signal validity, latitude, longitude, speed (kn), true course and

date. The GPS was switched on by the microcontroller via a NP transistor completing the earth of the GPS

(Figure 2). The controller cannot by itself power many of the components as they generally required a current

greater than the maximum current that can safely be supplied by any of the microcontroller’s pins (< 40 mA).

It is far better practice to use the low current provided by the controller pins to turn a switch (NP transistor in

this case) on and off and allow greater currents to flow through this switch directly from the power source

21

(like turning on a light switch at home). This use of an NP transistor as a switch is discussed further below

under section “Additional supporting components”.

Temperature Sensor
The temperature sensor chosen was a High-Precision Digital Thermometer (model number DS1631A). The

DS1631A digital thermometer provides 9, 10, 11, or 12-bit temperature readings over a -55°C to +125°C

range with an accuracy of ±0.5°C from 0°C to +70°C with 3.0V ≤ VDD ≤ 5.5V. The DS1631A automatically

begins taking temperature measurements at power-up, which allows it to function as a stand-alone

thermostat. Unit cost was $4. The Thermometer was switched on by the microcontroller via a NT transistor

completing the power circuit (Figure 2). Trials of the DS1631A demonstrated that each unit required

calibration.

Data Storage
For data storage the microSD (Secure Digital) (https://simple.wikipedia.org/wiki/Secure_Digital_card) cards are the smallest storage cards available, measuring

only 15 mm × 11 mm × 1 mm. Since, they can store information without continued power supply they were

considered a perfect media for incorporation into the POTBot v1. The “Openlog” breakout board from

SparkFun (https://www.sparkfun.com/products/13712) is a low cost (~$15), open source data logger that

works over a simple serial connection and supports microSD cards up to 64GB. The Openlog can store or

“log” large amounts of serial data (>MegaBytes). Upon power up it can be provided with information over a

serial port that it will automatically record onto a microSD card. A pre-stored configuration file

(“CONFIG.TXT”) saved to the microSD can be used to adjust the behaviour of the Openlog. In POTBot v1

the configuration file contained a single line of information “4800,26,3,1“. This represented the baud rate for

communication between the Openlog and microcontroller (4800 bps), the ASCII value (in decimal form) for

the escape character (26 is ctrl+z), the number of escape characters required (3 represents hitting ctrl+z

three times to drop to command mode) and the system mode (set to 1 makes the Openlog append all

information in the same file - a value of 0 results in a new file being created every time the Openlog is

restarted). Using this breakout board to do all the complicated conversions and writing to the microSD

reduces the demand on the Arduino Controller and simplifies the process. The Openlog was activated by

the microcontroller via a NT transistor completing the power circuit (Figure 2).

Power Source
This project coincided with the expansion and popularisation of "lithium-ion” technology which was a major

benefit. Initially rechargeable nickel-cadmium (Ni-Cd) and nickel-metal hydride (Ni-Mh) batteries were

trialled to run the POTBot v1. Each AA battery produced 1.2 v, as such 3 AA batteries could be used to

produce 3.6 v or four could be used to approximate 5 v (4.8 v). Since the #4 808 camera chosen for use ran

on 3.7 v (they could handle up to 5.0 v) the latter option of 4.8 v was initially chosen. Generally a good

quality AA battery contained up to 1000 mAh of power, however these were relatively expensive at $15 - $25

each (4.8 v worth could therefore cost up to $100). One issue that was discovered with the Ni-Cd and Ni-Mh

22

batteries was that they could be overcharged and the four AA batteries could produce up to 5.4 v. Voltages

over 5.0 could permanently damage the circuitry and/or components of the POTBot. The continued use of

AA batteries as a power source was therefore considered less than optimal. This realisation coincided with

the increase in availability of lithium-ion polymer (Li-Po) batteries, which had the advantage over the previous

rechargeable batteries of being smaller, cheaper, more powerful (greater storage capacity) and they

provided a constant 3.7 v (other constant voltages are also available). For example 5000 mAh Li-Po

batteries can now be purchased for $30 on Ebay (five times the capacity for a third of the price of the old

high quality Ni-Mh batteries). Following on from the move to a Li-Po power source, the POTBot versions 2

and 3 were built around a ~3.5 v operating voltage. The power source chosen, based on its capacity and

physical size, was a 3.7 v, 3800 mAh Lithium Polymer Rechargeable Battery (Li-Po) with a built-in protection

circuit (PCM) to prevent over charging or over discharging and a unit cost of $18. In POTBot v4 a move

back to 5.0 v was made with the development of a large number of portable power packs designed for

mobile phone charging (phones require 5.0 v for charging). The high demand of these units worldwide due

to the wide use of mobile phones has resulted in their very low cost, while the high energy demands of

mobile phones has resulted in these units having capacities well beyond what was previously available (10

000 mAh is not uncommon). In POTBot v4 the power source is likely to be 5600 mAh with a built-in

protection circuit PCM and voltage converter at a unit cost of $25.

Additional Supporting Components
Additional components were required to allow the central control board to control the various components.

These included five NP transistors (FB 51 PN100) whose primary role was to act as switches. When the

Arduino board sends a small current to the transistor’s base pin it allows a connection to form across its two

other legs (collector – emitter) allowing a current to pass. With this behaviour the resistor is essentially

earthing its attached component and allowing it to run. Three, 220 Ohm resistors (band code = orange,

orange, brown, gold) were required to minimise the amount of current that flowed into the transistors as they

were “switched on” by the controller. The use of the resistors reduces excessive power draw by the

transistors. A complete wiring diagram is provided in Figure 2.

Water Proof Housing
Waterproof housings are generally very expensive due to the high pressure environment they operate in and

their need to be customised for a specific purpose. For the POTBot this was also the case as their housings

had some additional specifications, they required a clear end piece for the camera to film through and they

needed to be made of a material that would allow for the transmission of a satellite signal from the GPS (i.e.

non-conducting material). Initial investigations suggested that professional purpose built housings were far

too expensive to meet the low-cost demands of the project. The easiest and potentially the lowest cost

alternative was to re-purpose a waterproof container. Underwater torch housings were the first option trialled

(POTBot v1). Low cost underwater torches were available online and purchased to test their depth range.

Of the three models available that suited the dimensions the POTBot one model proved water tight to over

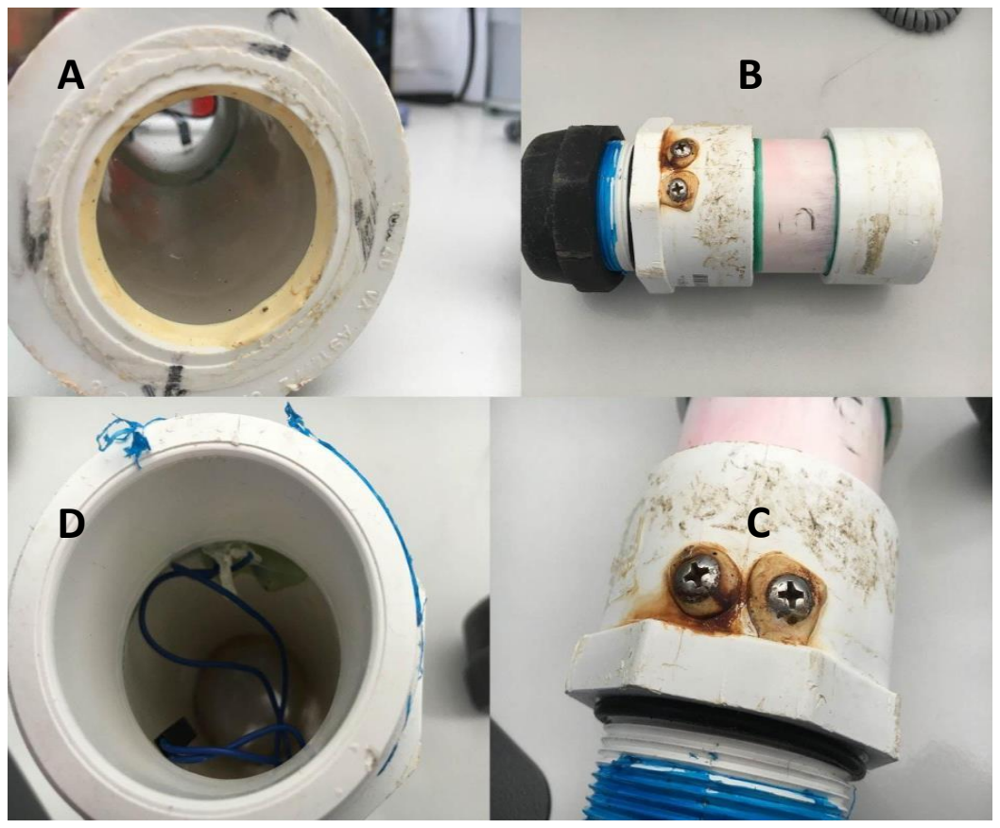
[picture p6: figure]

23

150 m and for only $35 was chosen as the housing option. However, six months later the O-rings in these

housings began to leak resulting in the destruction of a number of POTBot units. Upon further examination it

appears that this housing was no longer being manufactured and an alternative needed to be found. High-

pressure PVC pipe fittings were trialled next (POTBot versions 2 and 3). These required a small amount of

manufacturing time for construction and their lens plate had to be specifically milled out of 8 mm

polycarbonate. In materials they cost only about $30 per housing. Each housing was constructed from 110

mm of Vinidex 50 mm PVC Class 18 pipe (#13760), a class 18 Vinidex female-threaded 50 mm pipe v-

socket (50 2 Valve T/O Adaptor #34090), a class 18 Vinidex 50 x 40 mm reducing coupling (#35020) with the

40 mm section sawn off, Hansen Glass Fibre Reinforced Nylon 50 mm screw cap (#SC50) and an 8 mm

Perspex lens (Plate 2). These housings have been pressure tested and have remained water tight in depths

of 180 m (deeper depths have not been trialled). In each housing two small stainless-steel screws pierce the

wall to allow for an electrical current to be passed into the outside environment. A connection of current

between the two external pins allows the unit to detect the presence of water and thus whether it is

submerged or not. The housings have a screw-off end piece to allow for the removal of data and re-charging

of the Li-Po power source. In POTBot v4 a slightly larger housing will be required. Although still under

development it appears that the most appropriate construction material will again be PVC tubing.

Plate 2. High-pressure PVC pipe fittings constructed as a water proof housing used in POTBot v2 and 3, showing clockwise from top right: A. entire housing with black screw cap on left, B. water sensing screw pins towards the centre and lens located on the right; C. closer shot of the water sensing screw pins with

24

associated glue to ensure a tight seal; and D. internal view of the housing showing the wires connected to the internal aspect of the screw pins; front of the housing with its clear Perspex lens.

Placement in a lobster pot
An off-the-shelf non-metallic clamp system was sourced that allowed for a secure installation yet also a quick

and easy exchange of POTBot units. Polypropylene Stauff Gr. 7 clamps were fitted using stainless-steel

butterfly nuts to the rear-end of the lobster pots (Plate 3). This positioning provided the cameras an

unimpeded view of the surroundings as the pot descended and meant that the unit was approximately 400

mm above the seafloor when the pot settled on the bottom. The unit cost for a pair of clamps with

associated stainless steel threaded rod and butterfly nuts was ~$10.

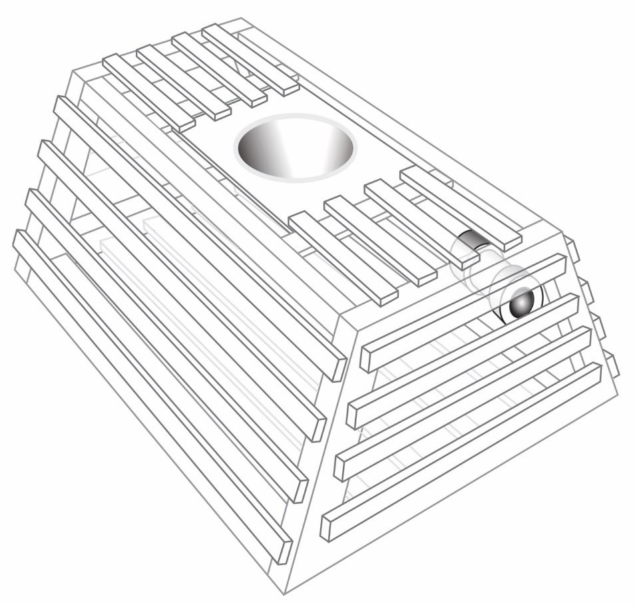
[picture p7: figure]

Plate 3. Schematic of a lobster pot showing the location of the POTBot.

Physical layout and construction
The POTBot was initially built on a breadboard and tested before a more robust prototype was developed.

Its basic structure consisted of the central Arduino mini which was attached to a power source and four

external components, the camera, the OpenLog, the GPS and the Thermistor (Figure 2). Upon the

successful completion of breadboard trials, printed circuit boards (PCBs) were developed using the freeware

25

software “ExpressPCB” (https://www.expresspcb.com/) with small production runs of PCB costing ~$35 each

(this cost reduces markedly in larger production runs and from other suppliers) (Figure 3, Plate 4). Each

PCB had holes for the attachment of the key components and their associated electrical components. The

advantage of the PCBs is that they allow for the robust connection of all components in a standardised

manner that is likely to withstand the rigors of being bounced around in a lobster pot.

Once soldered together the units were wrapped in protective foam insulation that kept them from moving

when placed within the PVC water proof housings. Each POTBot took approximately three hours to build,

load the code and placed in its housing. The batteries took about 3 hours to charge fully. The total cost of a

POTBot (components and housing) was less than $250 (Table 4).

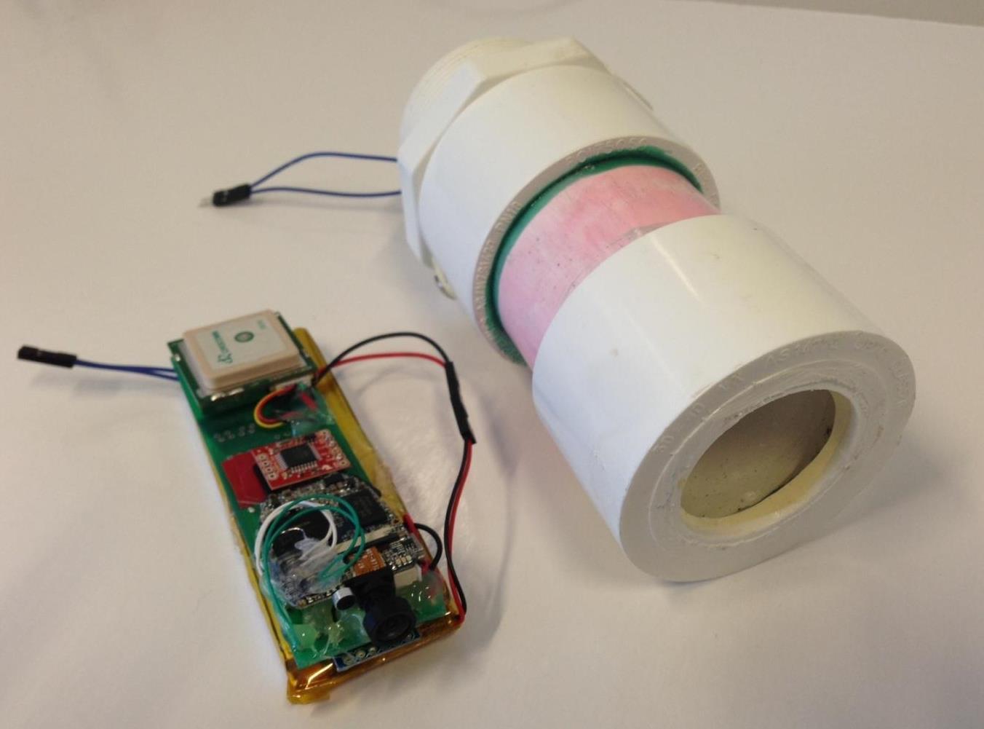
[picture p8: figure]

Plate 4. POTBot built on purpose-made PCB (green) with camera at the front, GPS visible towards the back and battery and Arduino mini located under the PCB; PVC underwater housing capable of deployments down to 180 m depth.

26

Table 4. Component costs for the development of POTBot version 3.

Component | Cost
Controller (Arduino mini) | $15
Camera (#16 808) | $45
GPS | $35
Thermometer | $4
Openlog | $15
2 * microSD (10 Gb) | $15
Underwater housing | $30
PCB | $35
LiPo battery | $18
Bracket | $10
5 * NP transistors | $0.25
3 * resistors | $0.05
Total | $222.30

Programming
The Arduino code is written in C++ and is uploaded to the controller using the Arduino software

(http://arduino.cc/en/Main/Software). The POTBot code has been provided in Appendix 2. The software

places the controller into a continuous loop of different states depending on the external stimuli it has

received (Figure 4).

- The initial state (S1) cycles the controller into and out of sleep mode every 2 seconds (to save

power) and tests, when awake, for input from the external pins to detect the presence of water.

- When detected the controller tests for water again, three successful sequential detections switches

the unit into state two (S2) and activates the camera for 10 mins.

- Upon the completion of filming the unit enters state three (S3). In this state it cycles between

sleeping and testing the environment, with continued detection of water keeping the unit in S3.

Every one hour in S3 the unit records its temperature. A one hour lag is used to allow the unit to

acclimate to the temperature of the surrounding environment. The unit records the temperature

along with the time and date (the latter two data from its internal memory).

- A failure to detect water when in S3 results in the unit moving into state four (S4). In S4 the POTBot

starts the GPS unit and continues to test for the presence of water.

- After a GPS fix is obtained the unit records its current location (retrieval location) and enters state

five (S5) when it tracks its location for up to three hours (Figure 4).

- If the unit detects water it returns to S2 and records its most recent location (deployment location).
- If the tracking time (while in S5) extends past three hours the unit re-enters S1 (it is assumed that if it

is not redeployed after three hours the pot will not be re-deployed for a considerable time and

tracking the unit to get its next deployment location will consume too much power).

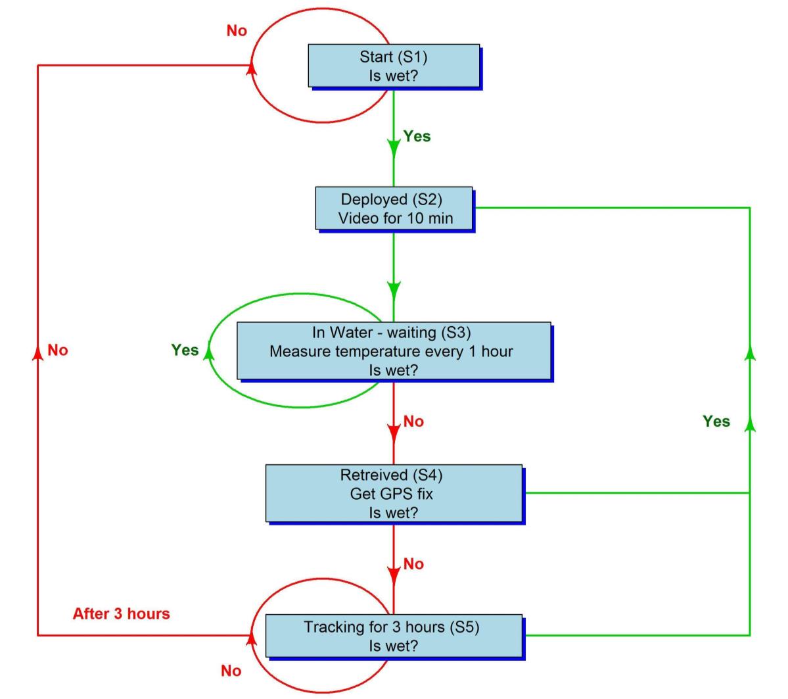
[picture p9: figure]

27

Figure 4. Flow diagram showing business rules followed by the POTBot versions 1-3 and its subsequent behaviour.

Objective 2. Trial implementation of system by industry to test concept.

A trial implementation of POTBots with the fishing industry occurred during 2013 and 2014 fishing seasons

and resulted in the collection of approximately 800 geo-referenced videos of benthic habitats and fish

communities (Figure 5). This total was accumulated from more than 90 separate deployment trips with 17

different commercial fishers. During this period the lobster fishers typically pulled and reset their lobster pots

every second day, thus collecting approximately 15 separate drop videos during a month-long camera

deployment. This suited the memory and battery capacity of the POTBots. On the basis of this, a program

was devised whereby fishers swapped a “used” POTBot over for a clean/charged model on a monthly basis,

at which point they were also provided with all of the information (geo-referencing videos and water

temperature readings) on a thumb drive.

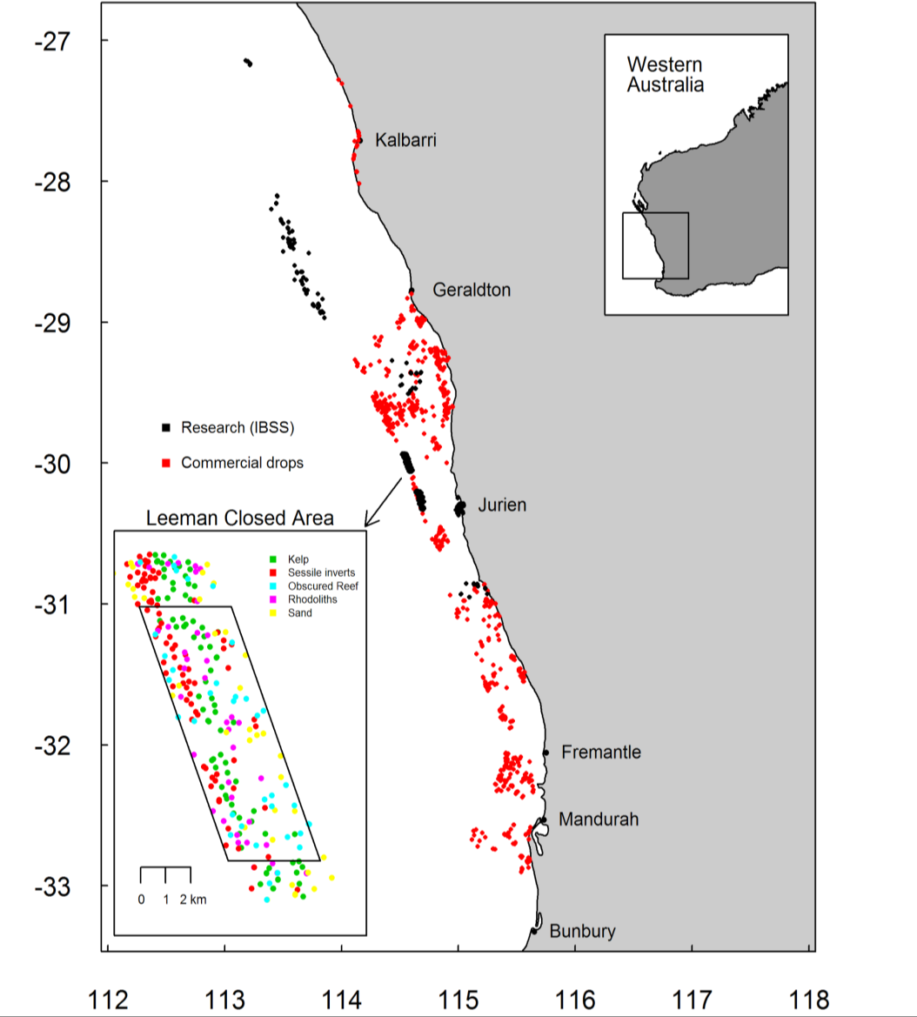
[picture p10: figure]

28

In addition to the industry collected data, pot cameras were widely used during research potting with more

than 500 fishery-independent data points collected. Habitat information has been collected throughout the

fishery, spanning almost 6 degrees in latitude and a range of water depths (Figure 5).

The vison obtained for each POTBot deployment was used to classify the surrounding habitat and ecology

based on a classification scheme developed under the Collaborative and Automated Tools for Analysis of

Marine Imagery (CATAMI) project. This classification scheme uses standardised terminology for describing

benthic substrates and biota in the marine environment (Althaus et al., 2015).

Figure 5. Map illustrating the spatial distribution of more than 1300 pot camera deployments made during research and normal commercial lobster fishing activities. The inset shows the key habitat categories observed inside and surrounding the research area at Leeman that is closed to lobster fishing and where high resolution bathymetric information was collected as part of FRDC 2008/013.

29

Performance of POTBot v2 and 3
In a standard commercial lobster fishing operation, where pots are pulled every second day (average over a

month) and are re-deployed with 30 mins of retrieval, the POTBot proved capable of recording the

information of approximately one month (15 deployments). After this length of time the unit began to run out

of power.

The majority of drops resulted in high quality footage which allowed the habitat to be easily observed. The

low light sensitivity of the cameras allowed the collection of footage, sufficient in quality to identify and

classify the habitat, in water depths down to 150 m, as long as the deployments occurred during the day. In

rough and turbid conditions, the footage was still capable of providing vision from which the habitat could be

described.

In 21% of the deployments the quality of the vision was not appropriate for classifying the habitat. The most

common cause of poor quality footage was the orientation of the pot when it landed on the seafloor (Figure

6). When the pot lands on uneven ground it can point at an awkward angle to the sea floor making it very

difficult to see the surrounding habitat. However, landing at an awkward angle did not always render the

footage useless as quite often the habitat could be assessed as the pot descended through the water

column towards the seafloor. Deployments during the night / very early morning and turbid conditions (due

to wave action in shallower locations) also caused a number of videos to be rendered useless (Figure 6).

System malfunctions were fairly uncommon (cause of only 15% of all problems, occurring in about 3% of all

deployments) and declined over the course of the project as the construction of the units became more

robust. The majority of malfunctions were related to power issues (batteries failing) or a soldered wire

coming loose.

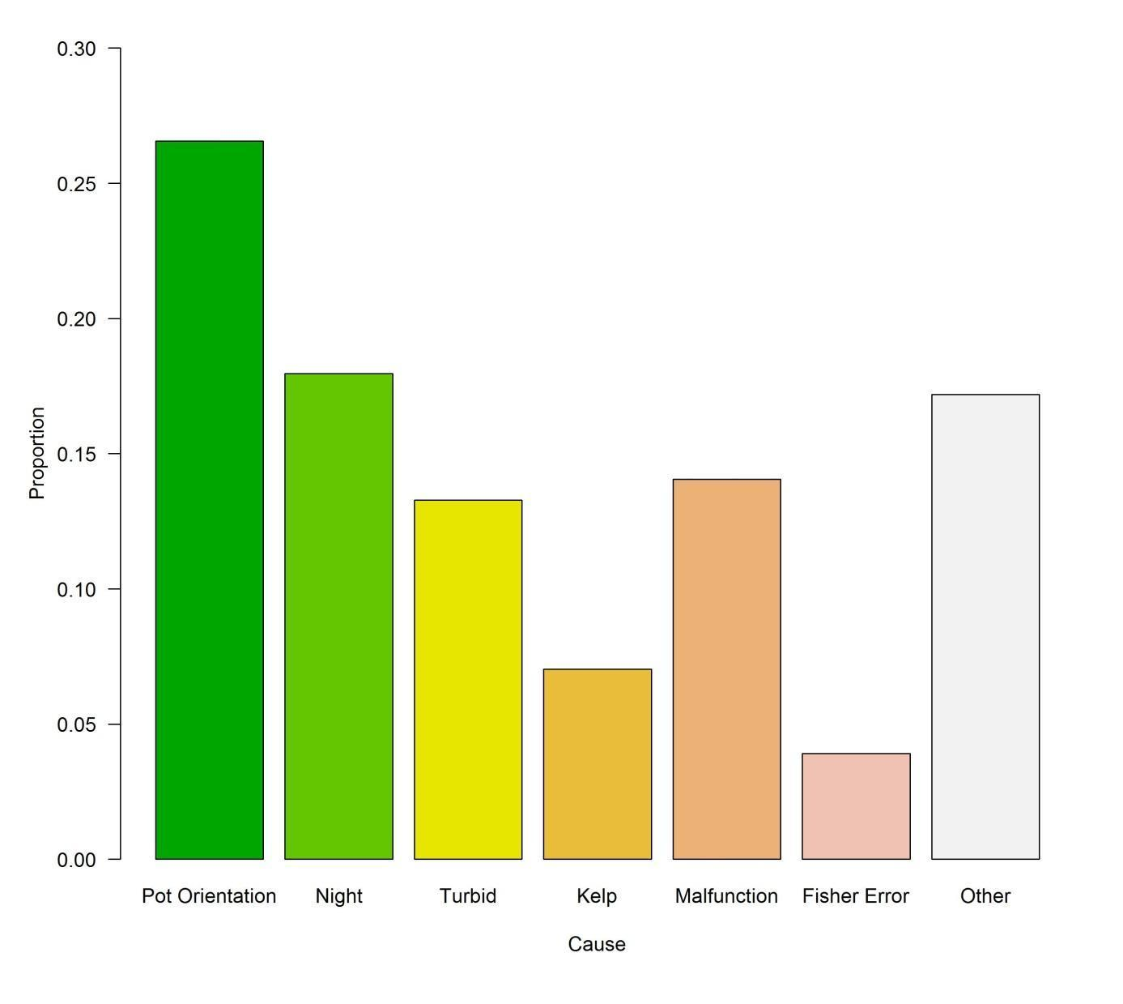
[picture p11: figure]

30

Figure 6. Relative causes resulting in a habitat classification not occurring from a POTBot deployment.

Objective 3. Cost-benefit analysis with conventional ground-truthing techniques.

Comparison of habitat mapping at the Leeman Closed area
The Leeman Closed area has been a focus for FD since 2010 as part of a study into the impacts of fishing

for lobsters in deep water (FRDC project 2008/013). Part of this research has required the fine-scale

mapping of the area using hydro-acoustic side-scan sonar, video tows, camera drops and POTBot data.

Collectively these data have resulted in the development of a very high-resolution habitat map. This study

has used this high-resolution map for comparison to assess the quality/accuracy of “lower quality” habitat

maps produced for the same area based on the reduced data sets such as that produced by the POTBot or

towed video studies. Two lower quality habitat maps were developed based on wither POTBot or

31

towed/drop camera samples. The maps were developed using based on inverse distance weighted

interpolation in the gstat package on the R platform (Pebesma, 2004; R Core Team, 2017). This method

assigned a probability of habitat type to each unknown 1 m² of the Leeman closed area based on the

assignment of surrounding known habitats (from samples) and their distance from the point to be estimated.

The greater the distance between known and estimate’s points lessens the influence of the known point on

the habitat assignment.

Comparisons between the high quality habitat map and lower quality maps (produced from either POTBot or

towed/drop sampling) were conducted by choosing 50 random locations from each of the lower quality

habitat maps. These points were compared with the habitat assignment for the same 1 m²
locations from the

high-resolution habitat map. The percentage of comparisons which matched between low and high quality

maps was used as a measure of the lower quality maps accuracy (i.e. assumes the high quality habitat map

was always correct).

The POTBot habitat data collected for this region were derived by placing units into research pots that were

being fished as part of the lobster sampling project. These data were therefore collected for only the cost of

the units (assuming they were only used this one time) [$250 for materials and $120 for construction by staff

for each POTBot], or at no cost if these units were lying idle as sampling occurred during the closed period of

the commercial fishery. As such the mapping of this entire area based on this data set cost a total of $7400

or nothing (the cost of processing the data is essentially the same as in the video tow/drop camera data set

and therefore not used in their comparison). This data set has been compared to that derived from drop

camera (Langlois et al., 2016) and tow-video surveys (Hovey et al., 2012) that were conducted in this region

as part of the marine mapping program. The cost of these surveys was $80,800, which was comprised of

vessel, staff and camera costs and was therefore at least about 10 times larger than the cost of the POTBot

based survey (assuming that both these surveys were the only time these camera systems were to be used).

From the two surveys 392 and 5072 data points were collected at a cost per data point of $18.88 and $15.93

for the POTBot and towed/drop surveys, respectively, under these assumptions. However it can be

considered that the cost for both camera systems could be removed as they were previously owned assets,

purchased for previous work. If the costs associated with the camera systems for each survey were

removed, the POTBot survey was conducted for no costs (since they were deployed and retrieved for zero

cost), while that of the drop camera and towed video surveys had a unit cost still of about $8 a sample (as

they required staff and vessel time for deployment).

Both sets of studies provided a good coverage of the study area at Leeman (Figure 7), although it is

noticeable that the tow video / drop camera data set had large numbers of sequential points that were not

heterogeneously spread across the area. Both data sets contained sufficient points to produce habitat maps

of the entire Leeman closed area (Figure 8). Although the resultant maps were overall relatively similar there

were a number of areas where different habitats were predicted to dominate. The map based on the

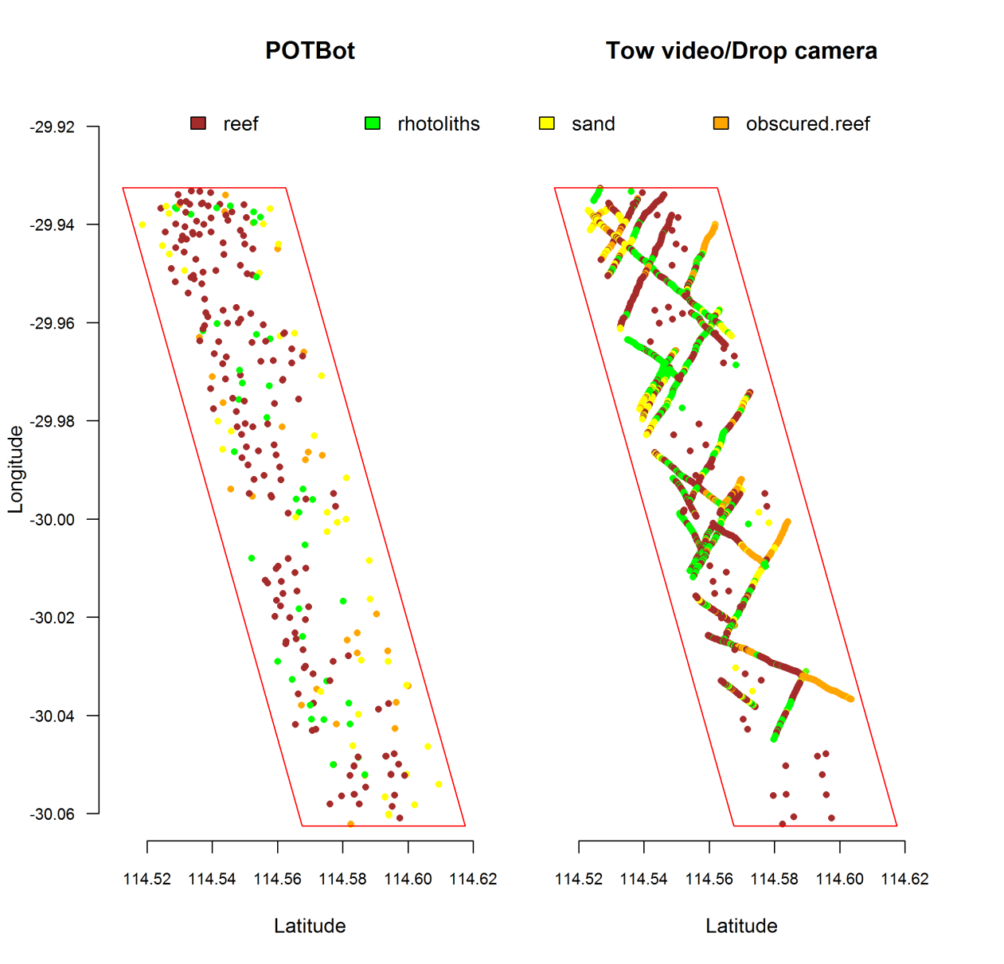
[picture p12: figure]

32

POTBot data set predicted that the western edge of the area was dominated by reef, while the eastern edge

by sand, whereas the map based on the towed video/drop camera predicted reef dominating the entire

southern region of the area, while the northern end was a mix of rhodoliths, obscured reef and reef (Figure

8). When randomly chosen points were selected from each habitat map and compared to the very high-

resolution habitat map (produced by all data sources as well as side-scan sonar) both habitat maps showed

good agreement with the high resolution map. The POTBot and drop camera/towed video studies agreed

with the high resolution map in 25% (36 comparisons) and 13% (38 comparisons) of comparisons,

respectively.

Figure 7. Maps showing the positions and habitat classification of samples collected by the POTBot (left) and drop camera / towed video (right) studies. The red border represents the limit of where the data were used to produce a habitat map.

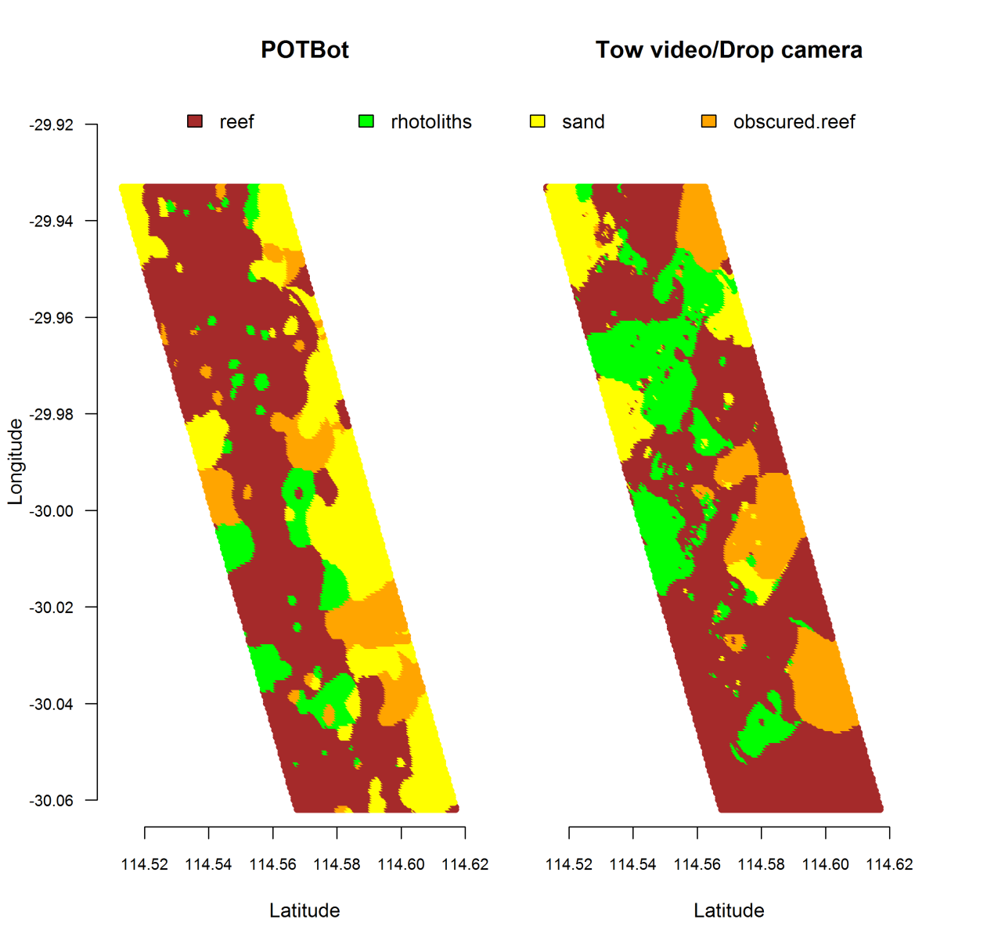
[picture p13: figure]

33

Figure 8. Habitat maps derived from data collected by the POTBot (left) and drop camera / towed video (right) studies.

Comparison of visual-based fin-fish monitoring
A second comparison was made between the fin-fish study conducted by Brooker et al. (submitted) which

was based on POTBot-derived data and a typical Baited Remote Underwater Video (BRUV)-based study

over a similarly wide spatial area (Langlois et al., 2012).

For the POTBot-based fin-fish study 398 videos were collected across 750 km of coastline from 19

commercial fishing vessels using 20 POTBot units. The collection of these data cost approximately $7400

and comprised only unit costs ($370 unit⁻¹

). This resulted in a cost per video sample of $18.59.

Furthermore, as there are essentially no on-going costs associated with this program, additional data can be

added at no extra costs and the costs per sample will to decline. For example, the costs associated with all

34

habitat samples collected during this study (1300 drops) have been collected at an individual sample cost of

$5.70. The additional costs associated with processing the footage and recording fish species has not been

included as it is consistent in this and the study by Langlois et al. (2012).

In the study by Langlois et al. (2012) footage was obtained using chartered vessels and university staff,

which resulted in a far greater cost per sample. To study their nine locations, which spanned 1500 km of

coastline, required 72 days of field work of which 54 days were on board charter commercial vessels. The

total cost of vessel hire was ~$162,000, cost for staff was ~57,600 and the BRUV units cost $30,000. The

total costs of $249,600 resulted in a unit cost of each sample being $173.33, or approximately 10 times that

for POTBot fin-fish vision.

35

## Discussion

## Objective 1: Development of a cost-effective system for obtaining geo-referenced

environmental information.

This project was successful in developing a low cost automated geo-referencing camera system that can be

deployed throughout a number of commercial fishing operations (i.e. any operation which deploys fishing

gear for an extended period of time). At a unit cost of approximately $250 this technology is far more

accessible for wide-scale implementation than other, less autonomous products available. For example the

popular system currently employed by a number of institutions (e.g. University of Oxford, England; Shahid

Beheshti University, Iran; University of Cape Town, South Africa; University of Palermo, Italy) for

implementation in baited remote underwater video systems (BRUVS; which still require user intervention to

start videos and do not geo-reference their footage) cost over $400. The POTBot can replace these units at

almost half the cost while also streamlining the process of deploying BRUVS due to their autonomous

nature. By adjusting the various parameters of the POTBot it can perform the functionality of a BRUV

system automatically, thus removing the need to start or stop any videos, or record their position.

The success of developing the POTBot is partly attributable to the recent rapid increase in the development

of micro-electronic systems and robotics. Over the course of the project both lithium-polymer batteries and

high-definition “spy” cameras became widely available in a range of sizes and at markedly reduced prices.

Micro-controllers have also increased in their diversity and reduced in cost. This has allowed the POTBot to

maintain a small size as well as low cost. For example, at the start of the project in 2013 most advanced

small high-definition cameras, sufficiently high in quality that they could be used in stereo video applications

to measure the lengths of moving fish, cost well in excess of $500. Now full high definition digital video

cameras with high enough frame rates to conduct the same analysis can be purchased for less than $50.

The small footprint of the POTBot has proved important for the fishers, primarily as they did not want marked

changes being made to their fishing gear (i.e. reductions in pot volume). Their size also makes it easy to

transport units back and forth between fishing vessels and the laboratory.

A fourth version of the POTBot is currently being developed. This model will be designed to eliminate some

of the issues associated with versions 1 – 3 and will hopefully lead to an expansion in the use of this

technology by other institutions. These earlier versions were quite complex to construct, as they needed

someone familiar with the process and soldiering experience. This led to substandard builds and thus units

that failed during operation. POTBot v4 will be designed to be more “plug-n-play” by containing a number of

plugs for one to connect the various components. Versions 1 – 3 also did not have the ability to detect

movement, an ability that adds substantial functionality. When deployed underwater, the addition of an

accelerometer and/or magnometer, allows the unit to be programmed to collect additional footage as it is

being retrieved. This process, in the context of a lobster fishing operation, will provide a better view

36

(generally 360o
) of the habitat as the camera will be facing directly down during the retrieval, thus removing

all issues associated with pots not landing flat when deployed (i.e. the cause of poor footage in 21% of failed

deployments). Detecting the retrieval process also allows for the GPS to be started earlier than previously,

getting a faster fix once the system breaks the surface and thus a better estimate of the deployment location.

The ability of the units sensing movement will also allow for reduced power consumption when on the

surface. Rather than track a vessel between retrieval and deployment to obtain the pot deployment location,

a unit sensitive to movement can obtain a location upon retrieval and then power-down the power-hungry

GPS and then monitor movement at low power cost. When the pot is picked up off the boat’s deck prior to

being deployed the unit can turn on the GPS and obtain the deployment position before the pot hits the

water.

Objective 2: Trial implementation of system by industry to test concept.

Analysis of both research and industry collected data is continuing. The habitats observed in most of the

videos collected have been analysed based on their percentage contribution. The collated habitat

information is providing a map of the key habitats fishers operate in across the extent of the fishery and

currently being used to validate the fishery-wide habitat maps that have been developed from the outputs of

a previous FRDC project (2008/013). These projects have directly resulted in the Marine Stewardship

Council certification of the WCRLMF becoming free, for the first time, of any conditions under Principle 2

(Ecosystems).

Trial implementation of the POTBot has highlighted the various limitations in the units which most commonly

led to poor footage being obtained. The main causes of issues were the orientation of the pot on the

seafloor, night-time deployments and camera malfunctions. The fourth version of the POTBot will aim to

improve the performance of the system as well as making it more user friendly to both construct and to

adjust the programming. In the most recent POTBot version (v3) all of the components were soldered to the

Printed Circuit Board (PCB) and only the battery is connected via a plug. Adjusting the parameters that

control the behaviour of the system requires a re-loading of the software via the Arduino software. In

POTBot v4 the aim will be to develop a PCB that can be populated with the various components by a

professional manufacturing company at low cost, including a number of plugs, which will improve the

structural integrity of the unit. The plugs will also allow for the attachment of a camera, GPS and battery by

the end user. This has the advantages of allowing the end user to attach the various components in

locations that suit their application and water proof housing. The parameters controlling the unit will be stored

on the microSD card in a text file which is easily modified by any user without need for an understanding of

C++ code or the Arduino software. For example, in the future to adjust the time length of the video taken the

microSD card needs to be removed from the POTBot and plugged directly into a computer. A file on the

microSD then can be opened in any of a number of common software programs (e.g. notepad or word) and

the video length changed in a few keystrokes. Once the card is re-inserted into the POTBot and power

37

supplied, the unit will automatically adjust its programming to suit the new video run-time.

Examination of fish community data from POTBot deployments highlighted the units’ versatility and cost-

effectiveness as a fisheries-independent monitoring tool that can be deployed using existing infrastructure.

Although comparison against spatio-temporal variation in similar fisheries-independent or -dependent indices

is required, preliminary results suggest that the method has potential as an alternative means for monitoring

relative abundance of fin-fish. Such data could be beneficial for stock assessment modelling and is highly

applicable in both developed and developing countries.

A recent marine heat-wave in 2010/11 has resulted in a marked change in the benthic biota in the Kalbarri

region (Wernberg et al., 2013). The result of this change in habitat has potential flow-on effects for the

associated faunal compositions, thus affecting important commercial and recreational fisheries (e.g. lobster,

abalone and scallops). However, due to the remoteness of this area and the fact that it is in a submerged

environment there is little information available to determine to what extent the habitat has changed. Some

data are available for the area from POTBots deployment and this has been useful in assessing that a

change has indeed occurred. The fact that these data were collected at minimal cost (they were deployed

during Western Rock Lobster fishing operations at zero cost) and the purpose of the collection was not

specifically designed to determine the impact of a marine heat-wave (we did not know of its imminent arrival)

highlights the value of maintaining the project into the future.

It is expected that the future version (v4) of the POTBot will be completed by the end of 2017. Their

implementation into a number of studies has already been planned and plans for the units have been

requested from a number of national and international research centres including (University of Western

Australia, Murdoch University, University of New Caledonia and the Nova Scotian Government). It is hoped

that, following the publication of a number of papers (one has been submitted), interest in this novel research

tool will continue to grow.

Objective 3: Cost-benefit analysis with conventional ground-truthing techniques.

The better performance of the map produced from POTBot data compared to that from drop camera/towed

video data was possibly due to the random nature of the former’s deployment. This resulted in the data

being spaced evenly over much of the region (see Figure 7), thus providing the geo-spatial model

information across the entire area. The towed video component however was tightly linked spatially to

subsequent samples (collected in strings) and therefore, although towed videos resulted in large numbers of

samples, these are tightly grouped together and did not homogenously cover the entire area. The result of

this was that areas such as the lower eastern edge of the region being studied had very little coverage from

the towed video/drop camera data set, and subsequently the habitats predicted for this region were generally

incorrect.

The mapping of the Leeman Closed area using POTBot data showed that, especially if an area is being

38

fished for a separate purpose, the use of POTBots can produce fairly accurate habitat maps far cheaper

when compared to the more traditional techniques. They also have the potential to continually collect data

as the fishery will return to similar areas each season, as against once-off research studies. This is

especially important under the guise of climate change as progressive increases in water temperatures will

continue in this area as it is one of the hotspots of water temperature increases (Hobday and Pecl 2013) and

are very likely to result in changes in the marine habitat.

A limitation of the POTBot project however, is that the exact placement of the system is at the mercy of the

fishing fleet, and units may therefore not be deployed in areas where the target species does not commonly

aggregate. This also has implication when the area to be mapped is located within an area closed to fishing

as again the fishing fleet cannot enter.

For sampling fish populations BRUV footage, although far more expensive than POTBot derived footage,

has some advantages, similar to that discussed above for the mapping comparison, in that they can be

placed when and where the researches want them to go. Another advantage is that most BRUV systems

are set up to collect stereo footage which allows for (but was not used in the case of Langlois et al. [2010])

the estimation of fish length. The POTBot sampling also had some advantages over that produced by the

BRUVs. By the nature of commercial fishing, POTBots were set in a range of weather conditions. As a

result Brooker et al (submitted) discovered that marked changes in fish abundance can occur in response to

changing ocean conditions. This fact has never been reported from BRUV-based studies as these are

generally conducted under relatively optimal weather conditions. Furthermore, although stereo vison is not

obtained by POTBots, recent papers using known ratios of fish length to eye diameter show that the POTBot

vison can be used to derive broad estimates of fish length on a scale that is appropriate for a number of

activities (i.e. determining juvenile to adult ratios) (Zeidberg, 2004; Richardson et al., 2015).

The comparison between two fin-fish projects suggests that the monitoring of marine fauna can be

conducted using POTBots at a fraction of the cost than using BRUVs, so long as the area of the study is

shared with a commercial fishery willing to adopt the POTBot fishing program. In the case of the Langlois et

al. (2012) study, only half of their study region overlaps with the WCRLMF, and they would have needed the

associated help of fishers in the South Coast Crustacean Fishery to encompass their entire study region.

## Conclusion

This project has produced an autonomous geo-referencing camera system which has been shown to provide

low cost monitoring of the habitats and fish communities throughout the WCRLMF. Their continued use will

provide information for the assessment of climate change effects, such as the habitat changes that have

occurred in the Kalbarri region following the 2011 marine heat wave (Wernberg et al., 2013). The usability

(usefulness and value) of the system is highlighted by the fact that a number of other institutions, both

39

nationally and internationally, have expressed their interest in acquiring this technology for use in their

research operations.

## References

Althaus, F., Hill, N., Ferrari, R., Edwards, L., Przeslawski, R., Schönberg, C.H., Stuart-Smith, R., Barrett, N., Edgar, G., Colquhoun, J. and Tran, M., 2015. A standardised vocabulary for identifying benthic biota and substrata from underwater imagery: the CATAMI classification scheme. PloS one, 10(10), p.e0141039.

Brooker, M.A. (2014). Fisher deployed baited video: A spatially expansive view of fish communities throughout Australia’s west-coast bioregion. Honours Research Dissertation, Faculty of Science; The University of Western Australia. 83 pp.

Brooker, M.A., Langlois, T.J., de Lestang. S., Fairclough, D.V., McLean, D., Slawinski, D., and Pember., M.B. (submitted). Fisher deployed automated videos reveal the influence of natural and anthropogenic factors on broad-scale fish abundance distributions.

Bellchambers, L., 2010. The effect of western rock lobster fishing on the deepwater ecosystems of the west coast of Western Australia. Fisheries Department of WA, pp. 90.

Bellchambers, L.M. and Pember, M.B., 2014. Assessing the ecological impact of the western rock lobster fishery in fished and unfished areas. Department of Fisheries, Western Australia, pp. 254.

Hobday, A, Pecl, G. 2013. Identification of global marine hotspots: sentinels for change and vanguards for adaptation action. Reviews in Fish Biology and Fisheries, 1-11.

Hovey, R.K., Van Niel, K.P., Bellchambers, L.M. & Pember, M.B. (2012). Modelling deep water habitats to develop a spatially explicit, fine scale understanding of the distribution of the western rock lobster, Panulirus cygnus. (http://paperpile.com/b/L9GTVH/VCxrZ) PloS one, (http://paperpile.com/b/L9GTVH/VCxrZ) 7, (http://paperpile.com/b/L9GTVH/VCxrZ) e34476. (http://paperpile.com/b/L9GTVH/VCxrZ)

Langlois, T.J., Harvey, E.S., Fitzpatrick, B., Meeuwig, J.J., Shedrawi, G. & Watson, D.L. (2010). Cost-efficient sampling of fish assemblages: comparison of baited video stations and diver video transects. Aquatic Biology, (http://paperpile.com/b/L9GTVH/W6t0L) 9, (http://paperpile.com/b/L9GTVH/W6t0L) 155–168. (http://paperpile.com/b/L9GTVH/W6t0L)

Langlois, T.J., Harvey, E.S., Radford, B.T., Van Niel, K.P., Meeuwig, J.J., Pearce, A.F., Rousseaux, C.S.G. & Kendrick, G.A. (2012). Consistent abundance distributions of marine fishes in an old, climatically buffered, infertile seascape. (http://paperpile.com/b/L9GTVH/sxdB6) Global Ecology and Biogeography, (http://paperpile.com/b/L9GTVH/sxdB6) 21, (http://paperpile.com/b/L9GTVH/sxdB6) 886–897. (http://paperpile.com/b/L9GTVH/sxdB6)

Langlois, T.J., Heyns-Veale, E.R., Parker, D., Götz, A., Bernard, A.T.F. and Harvey, E.S., 2016. Insights from baited video sampling of temperate reef fishes: how biased are angling surveys?

Metcalf, S.J., Pember, M.B. and Bellchambers, L.M., 2011. Identifying indicators of the effects of fishing using alternative models, uncertainty, and aggregation error. ICES Journal of Marine Science, 68, pp.1417-1425.

Pebesma, E.J., 2004. Multivariable geostatistics in S: the gstat package. Computers & Geosciences, 30: 683-691.

R Core Team (2017). R: A language and environment for statistical computing. R Foundation for Statistical

40

Computing, Vienna, Austria. URL https://www.R-project.org/.

Richardson, J. R., Shears, N. T., and Taylor, R. B. (2015). Using relative eye size to estimate the length of fish from a single camera image. Marine Ecology Progress Series, 538, 213-219.

Wernberg, T., Smale, D.A., Tuya, F., Thomsen, M.S., Langlois, T.J., de Bettignies, T., Bennett, S. & Rousseaux, C.S. (2013). An extreme climatic event alters marine ecosystem structure in a global biodiversity hotspot. (http://paperpile.com/b/L9GTVH/OaZHI) Nature Climate Change, (http://paperpile.com/b/L9GTVH/OaZHI) 3, (http://paperpile.com/b/L9GTVH/OaZHI) 78–82. (http://paperpile.com/b/L9GTVH/OaZHI)

Zeidberg, L. D. (2004). Allometry measurements from in situ video recordings can determine the size and swimming speeds of juvenile and adult squid Loligo opalescens (Cephalopoda: Myopsida). Journal of experimental biology, 207(24), 4195-4203.

41

## Implications

The POTBot system proved valuable in the mapping and long-term monitoring of marine habitats. The

advent of the marine heatwave highlighted the benefits of long-term datasets tracking the floral and faunal

compositions of the marine environment, data that can only be collected by a system such as the POTBot.

The continued use of this technology by multiple institutions around Australia will prove invaluable in

assessing the longer-term impacts of global warming.

## Recommendations

The POTBot system developed during this study proved to be an extremely useful research tool. This has

been highlighted by the fact that data collected during this project have already been used to describe the

faunal composition of teleosts along the mid-west coast of Australia, as well as to augment the development

of habitat maps throughout the same area.

Through the use of this technology information on habitats in remote areas has been recorded for the first

time, information that will be valuable when determining long-term environmental changes in the future.

Such a case has already occurred, following the marine heatwave of 2011.

It is recommended that, when appropriate, this technology should be adopted by other research institutions

to gather this previously inhibitively expensive data and long term data sets should start to be collated.

## Further development

The most recent POTBot system developed during this study (v3) contained a few minor limitations, such as

no ability to determine its movement/orientation. Since the conclusion of the project, work has continued, in

conjunction with the University of Western Australia’s School of Electrical, Electronic and Computer

Engineering, in the development of an improved POTBot model that will be more robust, have added

capabilities and will be more user friendly. It is planned that the schematics of this model will be freely

available for use by other research organisations.

## Extension and Adoption

The POTBot program has been adopted by FD and is planned to be included as an annual project

(continued supply to fishers to increase habitat coverage). One scientific journal article and an Honours

thesis from UWA have been based on data collected from the POTBot program. Two additional papers are

currently under construction, and as more data are collected further papers will be developed. All habitat

data collected by the program have been provided to the Oceans Institute at UWA for their use in developing

habitat maps for the west coast of Australia. The data collected by commercial fishers using POTBots during

this project has already contributed to the development and validation of bioregion-wide distribution models

42

of benthic primary producers predicted from bathymetry datasets, which will be published shortly.

Presentations on this project have been provided to the West Australian fishing industry and wider scientific

community at a number of meetings including Western Rock Lobster Annual Management Meetings and the

9th (Canada) and 10th (Mexico) International Meeting on Lobster Biology and Management.

A number of other institutions have expressed their interest in obtaining units for use in their research

programs. These include UWA, Tasmanian Aquaculture and Fisheries Institute, the National Autonomous

University of Mexico, South Australian Research and Development Institute and Florida Fisheries and

Wildlife.

## Project Coverage

Preliminary details of the project have been communicated to both national and international audiences including ecologists, stock assessment scientists and fisheries managers with a presentation “POTBot: A cost effective approach to mapping habitats” being presented at

- The 9th International Conference and Workshop on Lobster Biology and Management (Bergen, Norway).
- Australian Marine Science Association 2011 Annual Conference (Fremantle, Australia)

Initial results of the project have been communicated in a poster presentation “An industry-based approach to regional-scale monitoring of benthic ecosystems” presented at both

- The 10th International Conference and Workshop on Lobster Biology and Management (Cancun, Mexico).
- The 10th International Temperate Reef Symposium (Perth, Australia)

Details of the project have also been widely communicated within the FD and nationally within the CSIRO.

A media statement introducing the project to the public was released in December 2011. As a result, the project received wide coverage on television (Channel 10), radio (ABC Rural; 6PR), and online media (below).

The West Australian online: http://au.news.yahoo.com/thewest/video/watch/27487441/12735368/51/

ScienceWA: http://www.sciencewa.net.au/topics/fisheries-a-water/item/1136-robots-used-to-spy-on-rock-lobster-pots (http://www.sciencewa.net.au/topics/fisheries-a-water/item/1136-robots-used-to-spy-on-rock-lobster-pots)

Perthnow: http://www.perthnow.com.au/news/special-features/underwater-robots-to-spy-on-fisheries/story-e6frg19l-1226214217898 (http://www.perthnow.com.au/news/special-features/underwater-robots-to-spy-on-fisheries/story-e6frg19l-1226214217898)

Couriermail online: http://www.couriermail.com.au/ipad/underwater-robots-to-spy-on-fisheries/story-fn6ck4a4-1226214548164 (http://www.couriermail.com.au/ipad/underwater-robots-to-spy-on-fisheries/story-fn6ck4a4-1226214548164)

Details of the project were also disseminated in the Department’s email newsletter WA Fish eNews (09/12/2011 ed.), which has a targeted subscription of more than 600 including many commercial fishers. A preliminary story has also been posted on the Department’s youtube channel. An updated video will be

43

posted before the end of the project http://www.youtube.com/user/fisherieswa/feed

## Project Materials Developed

Brooker, M.A., Langlois, T.J., de Lestang, S., Fairclough, D.V., McLean, D., Slawinski, D., Pember, M.B.

(submitted). Fisher deployed automated videos reveal the influence of natural and anthropogenic factors on

broad-scale fish abundance distributions.

Brooker, M.A. (2014). Fisher deployed baited video: A spatially expansive view of fish communities

throughout Australia’s west-coast bioregion. Honours Research Dissertation, Faculty of Science; The

University of Western Australia. 83 pp.

44

Appendix 1.

List of researchers and project staff:

Matthew Pember (formerly with DPIRD).

Senior Resource Access Officer.

Western Australian Fishing Industry Council

Phone: +61 08 9432 7715

Fax: +61 08 9432 7700

Email: rao@wafic.org.au

Simon de Lestang.

Principal Research Scientist.

Department of Primary Industries and Regional Development; Fisheries Division

Phone: +61 08 9203 0174

Email: Simon.delestang@fish.wa.gov.au

Dirk Slawinski.

Senior Experimental Scientist

Commonwealth Scientific and Industrial Research Organisation

Email: Dirk.Slawinski@csiro.au

45

Appendix 2. POTBot code.

See: https://github.com/sdelestang/POTBot

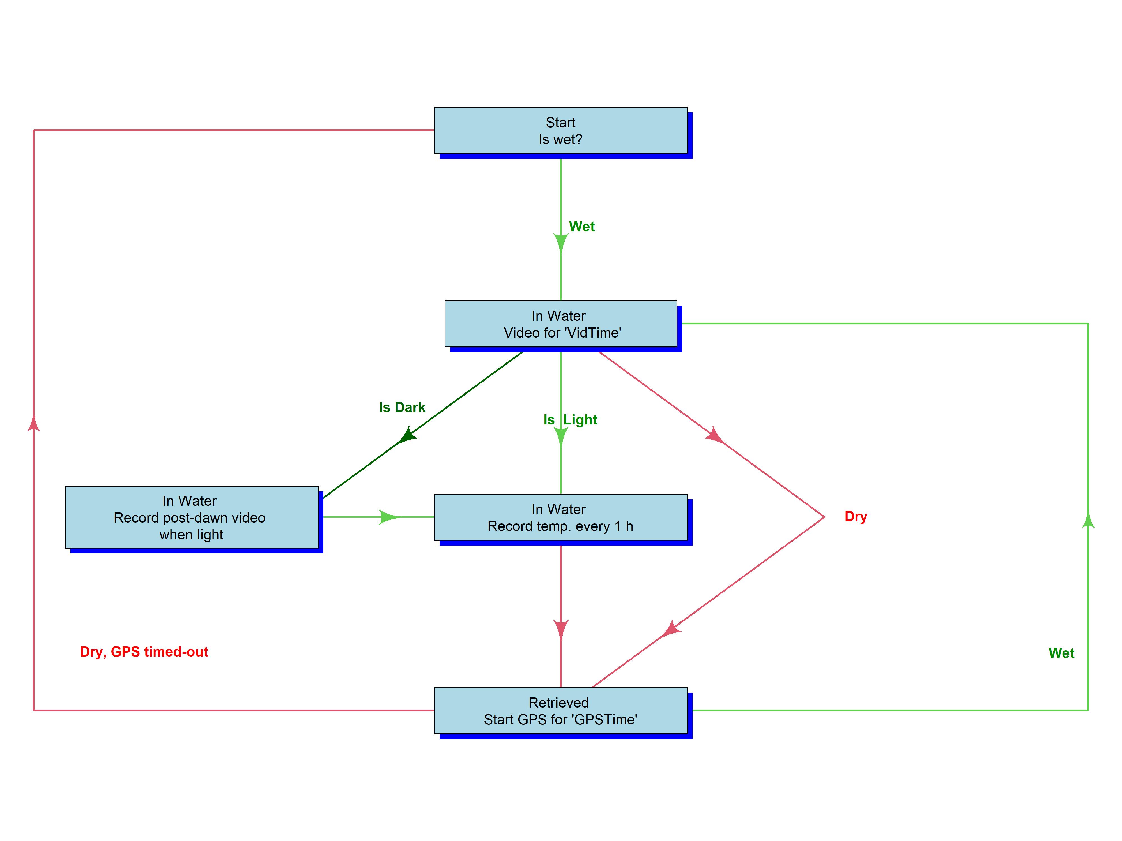
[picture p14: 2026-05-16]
docs/Flow Diagram PB IV.jpg

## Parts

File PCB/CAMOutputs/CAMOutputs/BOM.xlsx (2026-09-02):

Item # | *Designator | *Qty | Manufacturer | *Mfg Part # | Description / Value | *Package/Footprint | Link
1 | USB_PC | 1 | Amphenol FCI | 10118194-0001LF | USB Connectors 5P MICRO USB TYPE B RCPT W/ REAR PEGS | SMD | https://au.mouser.com/ProductDetail/Amphenol-FCI/10118194-0001LF?qs=Ywefl8B65e4FIdY8OWfRQA%3D%3D&countrycode=AU&currencycode=AUD

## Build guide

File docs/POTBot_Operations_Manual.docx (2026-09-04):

POTBot

Automated Underwater Camera System

Operations Manual

Firmware Version 10

Open-Source Freeware

github.com/sdelestang/POTBot

2026

# Contents

# Introduction

The POTBot is an automated underwater camera and environmental monitoring system designed for use in crustacean fisheries research. It is deployed inside lobster pots (fishing traps) to record video footage of pot contents, log water temperature, and capture GPS coordinates upon retrieval.

The system operates autonomously once powered on. A conductivity-based wet switch detects immersion, triggering video recording. Upon retrieval from the water, the unit activates its GPS module to log the pot’s location. Temperature is recorded periodically while the unit remains submerged.

This manual covers software installation, firmware configuration, field deployment, data retrieval, and camera setup. It applies to POTBot firmware version 10 (PB_CodeV10).

# System Overview

## Hardware Components

Component | Description
Microcontroller | Adafruit ItsyBitsy M0 Express
Camera | Mobius ActionCam
GPS Module | Serial GPS (9600 baud, via Serial1)
Real-Time Clock | Gravity RTC module (I²C)
Temperature Sensor | Dallas DS18B20 (OneWire, pin A1)
Flash Storage | Adafruit SPI Flash (onboard, FAT filesystem)
Status LED | Adafruit DotStar (single NeoPixel)
Wet Switch | Conductivity-based (analog read with digital excitation)

## Rear Panel Connections

The rear panel of each POTBot unit provides three connections, from left to right:

1. Micro-USB for the ItsyBitsy M0 microcontroller (firmware upload and serial data access).
2. Battery power connector (centre).
3. Micro-USB for the Mobius camera (video file access).

## Operational Flow

The diagram below illustrates the POTBot’s state machine. On power-up, the unit searches for GPS satellites to initialise the module. Once a lock is obtained, it enters a sleep/wake cycle monitoring the wet switch. Detection of water triggers video recording, followed by periodic temperature logging. When retrieved (dry), the GPS activates to record the retrieval position.


Figure 1. POTBot operational state diagram.

## LED Status Indicators

The onboard DotStar LED provides visual feedback on the unit’s current state:

LED Colour | Meaning
Green (startup) | Battery voltage above 4.0 V
Red (startup) | Battery voltage below 4.0 V — charge or replace battery
Yellow | Searching for GPS satellites
Purple | GPS lock acquired
Off | Normal operation / sleep mode

# Software Installation

## Arduino IDE

1. Download the firmware from GitHub. Navigate to https://github.com/sdelestang/POTBot and click the green “Code” button, then select “Download ZIP”. Save and extract the ZIP file to a convenient location on your computer (e.g. C:\POTBot).
2. Download and install Arduino IDE from https://www.arduino.cc/en/software.
3. Launch the IDE and follow any prompts to update to the latest version. This can typically be done without administrator permissions.

Note: Board and library installation may fail if the IDE is not updated first. Always update before proceeding.

## Board Support

1. Open File → Preferences. In the “Additional Boards Manager URLs” field, enter: https://adafruit.github.io/arduino-board-index/package_adafruit_index.json
2. Open Tools → Board → Boards Manager. Search for “Adafruit SAMD” and install the package.
3. Restart the IDE. Under Tools → Board → Adafruit SAMD, select “Adafruit ItsyBitsy M0” (may appear as “ItsyBitsy M0 Express” depending on the package version).

## Libraries

The following libraries must be installed via Sketch → Include Library → Manage Libraries:

- OneWire
- DallasTemperature
- Adafruit SleepyDog
- Adafruit SPIFlash (and its dependencies: SdFat – Adafruit Fork, Adafruit NeoPixel)
- TinyGPS++ (or TinyGPS depending on version)
- Adafruit DotStar (and its dependency: Adafruit BusIO)
- RTClib (required for Version 4 and later)

One additional library must be installed manually from a ZIP file: GravityRTC. This file is located in the Github repository: https://github.com/sdelestang/POTBot/tree/master/docs

Download this zip file and install via Sketch → Include Library → Add .ZIP Library and follow the prompts.

To verify installation, check File → Examples — installed libraries should appear with example sketches.

# Programming the POTBot

## Loading Firmware

1. Open the firmware sketch. In the extracted POTBot folder, navigate to Version10\PB_CodeV10\PB_CodeV10.ino and double-click to open it in Arduino IDE. Important: Arduino requires that the .ino file resides in a folder with the same name as the sketch. Do not move PB_CodeV10.ino out of its PB_CodeV10 folder, or the IDE will refuse to compile it. If you need to relocate the file, copy the entire PB_CodeV10 folder
2. Disconnect the battery from the POTBot.
3. Connect the POTBot to the computer using a micro-USB cable plugged into the left-hand port (ItsyBitsy board).
4. Under Tools → Port, select the port with the suffix “(Adafruit ItsyBitsy M0)”.
5. Verify that Tools → Board is set to “Adafruit ItsyBitsy M0”.
6. Click the Upload button (right-arrow icon, top-left). The IDE will compile and then upload the firmware. Progress is shown in the status bar.
7. On successful upload, open the Serial Monitor (magnifying glass icon, top-right) to verify the POTBot reports its firmware version and RTC time.

## Setting the Real-Time Clock

The onboard RTC maintains accurate time even when unpowered. It only needs to be set on first use or if the time drifts significantly. The GPS will also automatically correct the RTC when a reliable fix is obtained.

To manually set the RTC:

1. In the firmware sketch, locate the RTC calibration line (approximately line 113). Remove the comment markers so it reads:

rtc.adjustRtc(F(__DATE__), F(__TIME__));

2. Upload the firmware. This sets the RTC to the computer’s current date and time.
3. Immediately re-comment the line so it reads:

//rtc.adjustRtc(F(__DATE__), F(__TIME__));

4. Upload the firmware a second time. This prevents the RTC from resetting on every power cycle.

Note: If you forget to re-comment the line, the RTC will reset to the compile time every time the POTBot restarts.

## Configurable Parameters

The following parameters can be adjusted near the top of the firmware sketch (lines 88–91):

Parameter | Default | Unit | Description
VidTime | 2400 | seconds | Duration of video recording after deployment
GPSTime | 240 | minutes | Duration GPS remains active after retrieval before timeout
Dawn | 7 | hour (24h) | Start of daylight window for video assessment
Dusk | 17 | hour (24h) | End of daylight window for video assessment

Ensure each line ends with a semicolon after changing a value.

# Field Deployment

## Pre-Deployment Checklist

- Battery is fully charged (green LED on startup).
- SD card is inserted in the Mobius camera.
- Camera is configured correctly (see Section 8).
- Firmware is loaded and RTC time is correct.
- Previous data has been downloaded and cleared.

## Deployment Procedure

4. Connect the battery to the centre power connector on the rear panel.
5. The POTBot will power on and display the battery status LED (green = good, red = low).
6. The LED will turn yellow as the unit searches for GPS satellites. Wait for the LED to turn purple, indicating a successful GPS lock. After approximately one minute the LED will turn off and the unit is ready.
7. Place the POTBot into the lobster pot. When the wet switch detects immersion, the camera will begin recording for the configured video duration.

## Operational Behaviour

Once deployed, the POTBot operates autonomously through the following cycle:

- On immersion: records video for the configured duration (default 40 minutes).
- If deployed during darkness (outside the Dawn–Dusk window): a short additional video (2 minutes) is recorded once daylight is detected, to capture habitat imagery.
- While submerged: records water temperature at scheduled intervals (initially 2 hours after deployment, then at 23:00 daily).
- On retrieval (dry): activates GPS and records the first three position fixes. The GPS remains active for the configured timeout period (default 4 hours).
- If re-deployed before GPS timeout: records the last GPS position and begins a new video cycle.
- If GPS times out without re-deployment: the unit returns to its initial standby state.

Note: The RTC is automatically corrected from the GPS whenever a reliable fix is obtained with four or more satellites.

# Data Retrieval

## Downloading Video

4. Connect a micro-USB cable to the right-hand port on the rear panel (Mobius camera).
5. The camera will appear as a removable drive on your computer.
6. Copy all video files to the appropriate Teams folder.
7. Delete the files from the camera to free space for the next deployment.

## Downloading Metadata

8. Connect a micro-USB cable to the left-hand port on the rear panel (ItsyBitsy).
9. Open Arduino IDE and launch the Serial Monitor (magnifying glass icon) within 7 seconds of connection.
10. The POTBot will display its firmware version, RTC date/time, and begin monitoring the wet switch.
11. Type Print (case-sensitive) and press Enter. The unit will output all stored deployment data.
12. Select and copy all output text. Paste it into a Microsoft Word document, include the skipper name, location, and date in the title, and save to the Teams folder alongside the video files.
13. Type Clear to delete all stored data from flash memory, readying the unit for the next deployment.
14. Type Run to restart normal operation.

## Serial Monitor Commands

Command | Action
Print | Stops the POTBot and prints all stored data (GPS positions, deployment times, temperatures) to the Serial Monitor.
Clear | Stops the POTBot and deletes all stored data from the onboard flash memory.
Run | Restarts the POTBot and resumes normal wet-switch monitoring.

## Data Storage on Teams

All data and videos are stored on Microsoft Teams under:

Team Lobster / General / PotBot 2023 / Videos

Create a new folder for each deployment using the naming convention:

[LFB Number]_[DDMMYYYY]_[Camera ID]

For example, POTBot A027 deployed on 12 March 2023 to LFBF020 would be named: F020_12032023_A027

# Mobius Camera Configuration

Each Mobius ActionCam must be configured before its first use with a POTBot. This only needs to be done once per camera unless settings are reset.

## Setup Procedure

1. Download and install the mSetup software from: https://www.mytempfiles.info/mobius/
2. Ensure an SD card is inserted in the camera before connecting it to the computer. Make sure the SD card is formatted to fat32 regardless of SD card size. Windows will not allow this so for larger ( > 32g) use guiformat.exe (free online) http://ridgecrop.co.uk/index.htm?guiformat.htm
3. Connect the camera via USB. In mSetup, click the camera line at the top of the window (showing “E Capacity = …”). Note that often camera will appear in the window as a storage device (will show SD card storage capacity) to remedy press the shutter button on camera (front left) once and wait.
4. On the first configuration tab, set the file system to match the SD card format. For larger SD cards, it still must be FAT32.

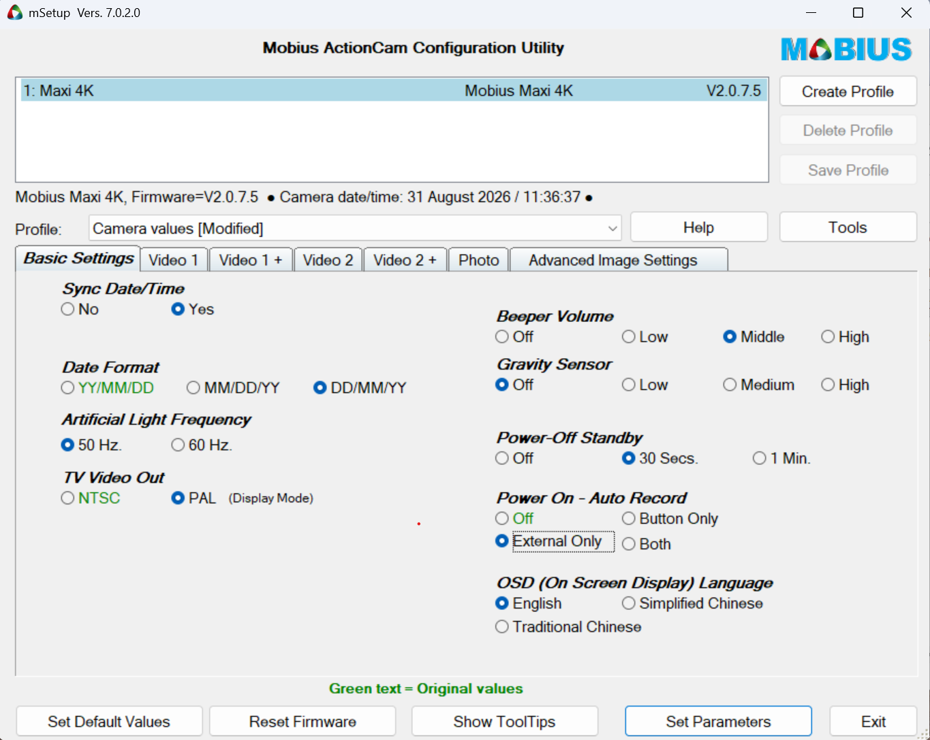
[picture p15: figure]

5. On the Video 1 tab, configure the recording settings as required for POTBot operation.

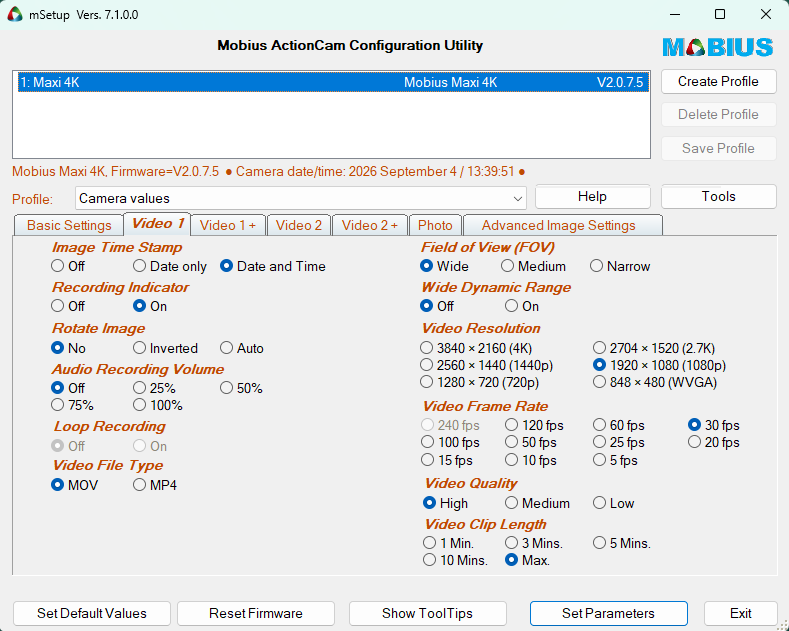
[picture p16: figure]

6. Click “Set Parameters” to save the configuration to the camera.

Note: When configuring multiple cameras, close and reopen mSetup between each camera to avoid cross-contamination of settings.

# Troubleshooting

## POTBot Does Not Power On

- Verify the battery is connected to the centre port and is charged.
- Check the battery voltage: a red LED on startup indicates low voltage. Replace or charge the battery.

## No GPS Lock

- Ensure the POTBot is outdoors with a clear view of the sky during initial GPS acquisition.
- The yellow LED will remain active while searching. Allow up to several minutes for a cold start.
- If the GPS consistently fails to lock, verify that the GPS module is connected to pin 5 and Serial1 is active.

## Camera Does Not Record

- Confirm the Mobius camera has an SD card inserted and is properly configured (see Section 7).
- Check the camera USB connection to the POTBot mainboard.
- Verify the wet switch is functioning: connect via Serial Monitor and observe whether the POTBot detects immersion.

## Serial Monitor Shows No Output

- The Serial Monitor must be opened within 7 seconds of connecting the USB cable.
- Ensure the correct COM port is selected under Tools → Port.
- Verify the baud rate is set to 9600 in the Serial Monitor.

## Firmware Upload Fails

- Ensure the correct board (Adafruit ItsyBitsy M0) and port are selected.
- Disconnect the battery before uploading.
- Try double-pressing the reset button on the ItsyBitsy to enter bootloader mode.

# Appendix: Pin Assignments

Variable | Pin | Function
curr_read | 0 (analog) | Wet switch: analog read for current sensing
temp_read | A1 | Dallas DS18B20 temperature sensor (OneWire)
curr_out | 11 | Wet switch: digital excitation output
curr_quite | 12 | Wet switch: reference current (held LOW)
camera | 7 | Mobius camera trigger
GPS | 5 | GPS module power control
LED | 13 | Onboard LED
pwrlsensor | 9 | Light sensor power
lsensor | A3 | Light sensor analog input
Voltage | A2 | Battery voltage monitor (via voltage divider)

POTBot — Page 1

POTBot Operations Manual OFFICIAL

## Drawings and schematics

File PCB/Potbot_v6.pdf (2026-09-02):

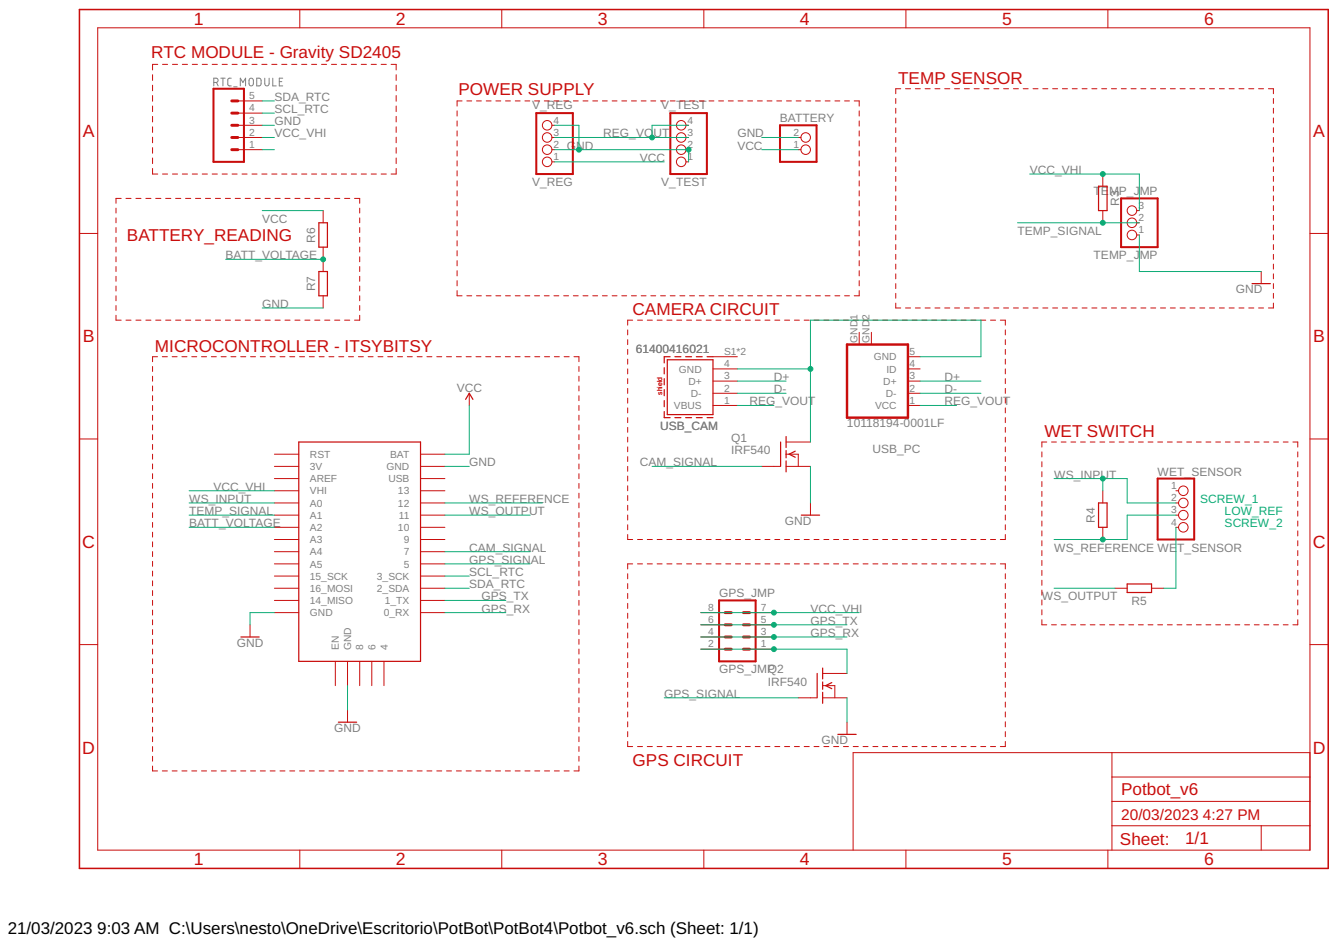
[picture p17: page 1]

21/03/2023 9:03 AM C:\Users\nesto\OneDrive\Escritorio\PotBot\PotBot4\Potbot_v6.sch (Sheet: 1/1)

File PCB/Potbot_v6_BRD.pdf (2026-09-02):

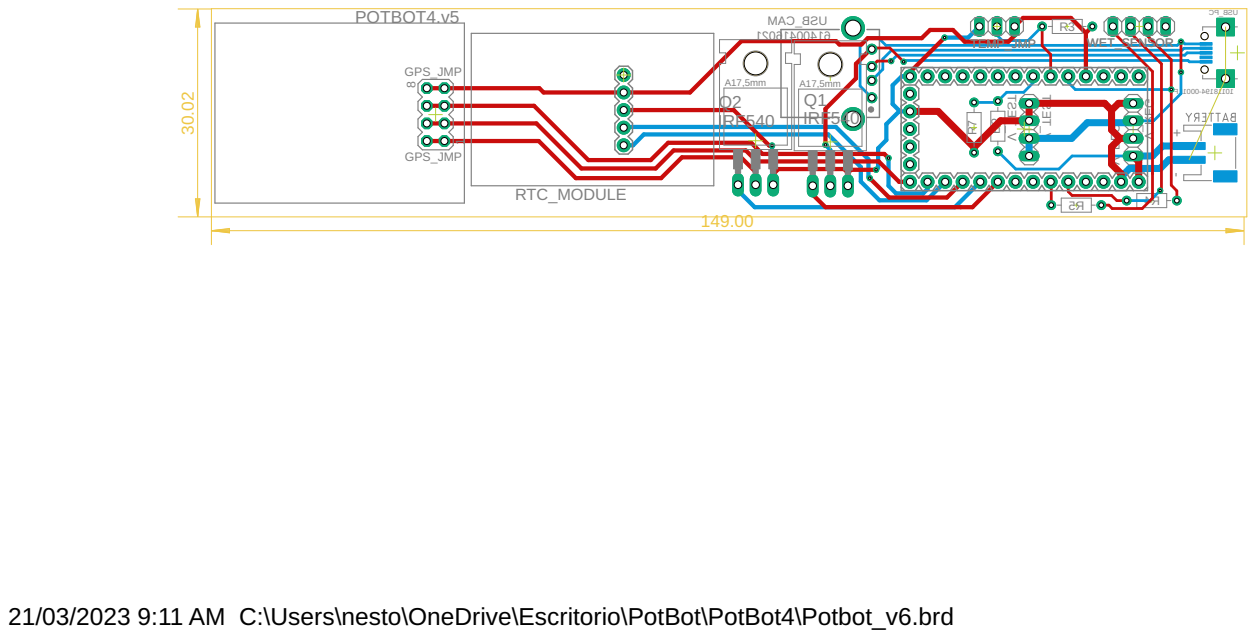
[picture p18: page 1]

21/03/2023 9:11 AM C:\Users\nesto\OneDrive\Escritorio\PotBot\PotBot4\Potbot_v6.brd

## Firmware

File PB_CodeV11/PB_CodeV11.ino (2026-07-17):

// select board AdaFruit ItsyBitsy MO
#include <Adafruit_SleepyDog.h>
// Data recording
#include <SPI.h>
#include <SdFat.h>
#include <Adafruit_SPIFlash.h>
// for flashTransport definition
#include "flash_config.h"

Adafruit_SPIFlash flash(&flashTransport);
// file system object from SdFat
FatVolume fatfs;
// Configuration for the datalogging file:
#define FILE_NAME      "data.csv"

// GPS
#include <TinyGPS++.h>
float lat,lon,sped;
int qual;
unsigned long age, date, Time;
static void print_date(TinyGPSPlus &gps);
TinyGPSPlus gps;// create gps object
// RTC
#include "GravityRtc.h"
#include "Wire.h"
GravityRtc rtc;              //RTC Initialization
// Control the NeoPixel
#include <Adafruit_DotStar.h>
#define NUMPIXELS 1   // There is only one pixel on the board
#define DATAPIN    41
#define CLOCKPIN   40
Adafruit_DotStar strip(NUMPIXELS, DATAPIN, CLOCKPIN, DOTSTAR_BRG);

// Temperature sensor
#include <OneWire.h>
#include <DallasTemperature.h>
#define ONE_WIRE_BUS A1
OneWire oneWire(ONE_WIRE_BUS);
DallasTemperature sensors(&oneWire);

// Pins
int curr_read =    0;     // was 1 read if Current flows A1
int temp_read =    A1;    // new pin for temperature
int curr_out =     11;    //  current send
int curr_quite =   12;    //  stay low - provide reference current
int camera =   7;         //  was ??
int GPS =    5;           //  was 9. 
int LED =   13;           //  
int Current   =    0;     //  Record the current in
int pwrlsensor =   9;     // powerup the light sensor
int lsensor =     A3;     //  lightsensor

// Print , Clear, Run
int bootCount = 0;
String command = "Run";
int start_potbot = -1;        // Used to designate whether initial deployment has occurred or if the unit should wait. 
int vidtaken = 0;                    //  Used to determine whether a video has been taken in that loop.
int temptaken = 0;                   //  Used to determine whether a temperature recording has been taken in that hour.
unsigned long TimeDeployed = 0;     //    Record when the temperature was taken for a lag
unsigned long Time4Temperature = 0;     //    Record when the temperature was taken for a lag
int Deployed = 0;            //  Used to determine if just deployed
int DeployedNo = 0;  //  Number of times POTBot has been deployed
int Num = 0;         
bool BoOL = true;
int Retrieved = 0;            //  Used to determine if just retrieved
int FstGPSLock = 0;            //  Used to determine if just got a lock
bool Vid_early = false;             // To record whether the video was taken in the dark
String Text = "Hello";
float Lat = 0; float AvLat = 0;     // Average latitude of 5 positions
float Lon = 0; float AvLon = 0;     // Average longitude of 5 positions
unsigned long GPSstart = 0;
int sensorValue = 0;                // For voltage tracking
float voltage = 0;
float voltagevar = 0;
/////////////////////////////////////////////////////////////////////////////////////////////////////////////////////////////////
long VidTime = 600;      // Seconds
long GPSTime = 240;      // Minutes
int Dawn = 7;
int Dusk = 17;
/////////////////////////////////////////////////////////////////////////////////////////////////////////////////////////////////

// Protected deep sleep using watchdog standby
// Disables SysTick and USB during transition to prevent premature wake and resets
void lowPowerSleep(unsigned long ms) {
  Serial1.flush();                                      // finish any UART
  USBDevice.detach();                                   // prevent USB interference
  SysTick->CTRL &= ~SysTick_CTRL_TICKINT_Msk;          // disable SysTick interrupt
  Watchdog.sleep(ms);                                   // true standby sleep
  SysTick->CTRL |= SysTick_CTRL_TICKINT_Msk;           // re-enable SysTick
  USBDevice.attach();                                   // restore USB
}

void setup() {
   // Neo Pixel
   PrintTextNum("Boot count: ", ++bootCount);
   strip.begin();
   strip.setBrightness(0);
   strip.setPixelColor(0, strip.gamma32(strip.ColorHSV(28160)));
   strip.show();
  
   pinMode(curr_read, INPUT);
   pinMode(curr_out, OUTPUT);
   pinMode(curr_quite, OUTPUT);
   pinMode(camera, OUTPUT);
   pinMode(GPS, OUTPUT);
   pinMode(LED, OUTPUT);
   pinMode(temp_read, INPUT);
   pinMode(lsensor, INPUT);
   pinMode(pwrlsensor, OUTPUT);
   
   rtc.setup();
   
  Serial.begin(9600);
  sensors.begin();
  delay(1000);
  // Initialize flash library and check its chip ID.
  if (!flash.begin()) {
    Serial.println("Error, failed to initialize flash chip!");
    while(1) delay(1);
  }

  // First call begin to mount the filesystem.
  if (!fatfs.begin(&flash)) {
    Serial.println("Error, failed to mount newly formatted filesystem!");
    Serial.println("Was the flash chip formatted with the fatfs_format example?");
    while(1) delay(1);
  }

  Serial1.begin(9600); // connect gps sensor

  // Check voltage — ensure GPS and camera are off first
  digitalWrite(GPS, LOW);
  digitalWrite(camera, LOW);
  delay(500);
  // Quick read for LED indicator
  analogRead(A2);
  delay(100);
  sensorValue = analogRead(A2);
  voltage = sensorValue * (3.3 / 1023.0) * 2.0;
  // Only log to file when on battery — USB gives misleading readings
  if(!Serial) { PrintVoltageDF("setup"); }
  // LED indicator
  if(voltage > 4.0) {
    strip.setBrightness(100);
    strip.setPixelColor(0, strip.gamma32(strip.ColorHSV(0)));  // Green
    strip.show();
  } else {
    strip.setBrightness(100);
    strip.setPixelColor(0, strip.gamma32(strip.ColorHSV(20480)));  // Red
    strip.show();
  }
  delay(5000);
  Serial.println("The POTBot is loaded with code V11.");
  Serial.print("It will film for ");Serial.print(VidTime/60);Serial.println(" minutes when deployed.");
  PrintDate("The RTC Date/Time is: ");
  Serial.println("To stop the POTBot and print out stored data enter 'Print'.");
  Serial.println("To stop the POTBot clear data enter 'Clear'.");
  strip.setBrightness(0);
  strip.show();
}

void loop() {
    if(!Serial){ lowPowerSleep(1000);}
////////////////////////////////////////////////////////////////////////////////////////////////////////////////  
   // Reads input entered through the Serial Monitor     
   if(Serial.available())  { 
      command = Serial.readStringUntil('\n'); 
      command.trim();}
 // This prints the data storage if "Print" in entered through the serial Monitor     
   if(command.equals("Print")){
      File32 dataFile = fatfs.open(FILE_NAME, FILE_READ);
      if (dataFile) {
      Serial.println(" "); Serial.println("Opened file, printing contents below:");Serial.println(" "); 
      while (dataFile.available()) {
       char c = dataFile.read();
       Serial.print(c);
    } }  else {
    Serial.print("Failed to open file \"");    Serial.print(FILE_NAME);   Serial.println("\" !! Does it exist?");
  }
     delay(1000);
     command = "Finished";
      }  
 // This clear the data storage if "Clear" in entered through the serial Monitor     
   if(command.equals("Clear")){
     Serial.println(" "); Serial.println("Deleting data file");Serial.println(" "); 
     if(!fatfs.remove("data.csv")) {
        Serial.println("Error, couldn't delete test.txt file!");
        while(1) yield();
       }
    delay(1000);
    command = "Finished"; 
      }  

// Initial GPS search to try and get a lock and improve subsequent gps efficiency.
while(start_potbot == -1 && CommandRun()) {  
   digitalWrite(GPS, HIGH);  // Start the GPS
   strip.setBrightness(100);
   strip.setPixelColor(0, strip.gamma32(strip.ColorHSV(10922))); // Yellow when searching
   strip.show();
   
   // Read ALL available bytes — drain the serial buffer
   while(Serial1.available()){
    if(gps.encode(Serial1.read())) {
      if(gps.location.isUpdated() && gps.satellites.value() >= 3) {
        lat = gps.location.lat();
        lon = gps.location.lng(); 
        sped = gps.speed.mps();
        qual = gps.satellites.value();
        strip.setPixelColor(0, strip.gamma32(strip.ColorHSV(54613))); // Purple
        strip.show();
        // Set RTC now while GPS time is fresh, then wait for LED display
        rtc.read();
        if(gpsFixIsReliable()) { resetRTC(); delay(100);}
        delay(60000);                // Wait one minute with the led on to highlight a connection has been made

  digitalWrite(GPS, LOW);  // Turn off the GPS
  Serial.println("Satellites found and GPS initiated. Ready to be deployed.");
  strip.setBrightness(0);
  strip.show();
  start_potbot = 0;
  break;  // exit inner while
        }}}
}

      
//////////////////////////////////////////////////////////////////////////////////////////////////////////////////
// Test is wet
      while(inwater() && CommandRun()) {                  // Camera is wet and POTBot set to "Run"
        rtc.read();
        start_potbot = 1;                                 // Once deployed start POTBot on normal cycle so it will enter the GPS once retrieved.
        FstGPSLock=0;
        if(Deployed==0) {                                 //  Has just been deployed and not yet taken video
          DeployedNo += 1;
          PrintDate("I am in the water.");
          Time4Temperature = rtc.hour + 2.0;  // Set time to record temperature 2 hours after deployment
          if (Time4Temperature>23) { Time4Temperature = Time4Temperature-24;} 
          PrintDateDF("POTBot has been deployed. ", true);
          PrintTextNum("Deployment number: ",DeployedNo);
          if(DeployedNo>1){ PrintPosDF("Last GPS position recorded before deployment (Lat, Lon, Speed, NSat.): ", lat, lon, sped, qual);}
          }    
        Deployed=1; Retrieved=0;
        // Take video following deployment
        if(vidtaken==0){
          Vid_early = VidNowEarly(Dawn,Dusk);
          digitalWrite(camera, HIGH);
          delay(VidTime*1000);
          digitalWrite(camera, LOW);
          vidtaken=1;
          PrintDateDF("Video Taken.", false);
          delay(500);        // let voltage settle after camera off
          PrintVoltageDF("post-vid");
          }
        // Take second video at 9 am if first video was taken in the dark
         if(Vid_early && !VidNowEarly(11,Dusk)){
          digitalWrite(camera, HIGH);
          delay(120*1000);                                  // 120 seconds just to get the habitat
          digitalWrite(camera, LOW);
          Vid_early = false;
          PrintDate("Short Video Taken because deployment video was taken in the dark.");
          PrintDateDF("Short Video Taken because deployment video was taken in the dark.", false);
           }
         if(Time4Temperature==rtc.hour  &&  rtc.minute==0 && rtc.second<5){
          PrintTempDF();
          PrintDateDF(" Water temperature", false);
          delay(100);
          Time4Temperature = 23;
            } 
         if(!Serial){ lowPowerSleep(1000);}
        }            // In the water
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
